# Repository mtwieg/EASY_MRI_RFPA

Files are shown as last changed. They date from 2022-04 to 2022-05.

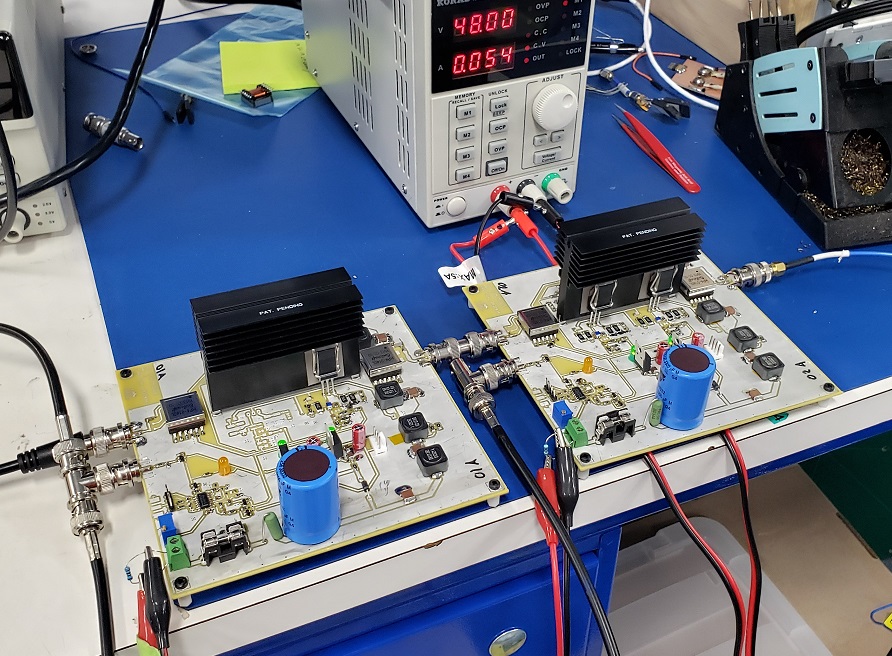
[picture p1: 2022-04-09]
Photos/full_test_setup.jpg

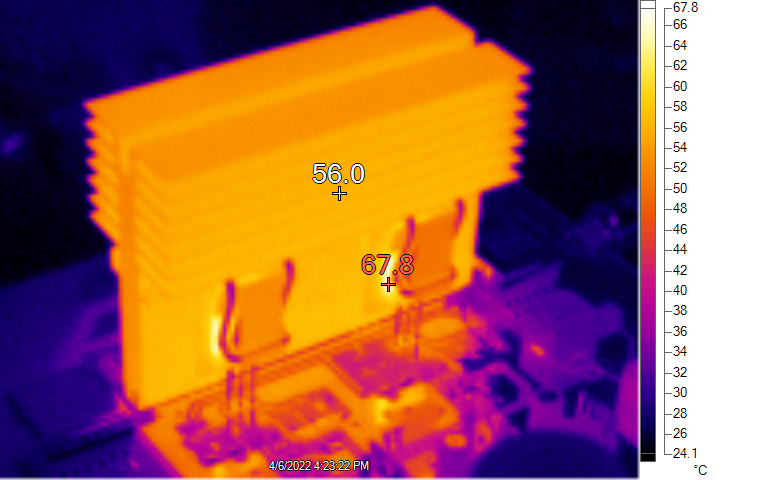
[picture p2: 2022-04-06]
Measurements and characterization/thermal_images_04_06_22/02_500us_20ms.png

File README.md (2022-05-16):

# EASY_MRI_RFPA
Click the "Wiki" tab above to view the tutorials and other info!

DISCLAIMER:
None of the designs in this repo have been tested or certified to any safety standards (IEC 60601-1, UL-94, etc). 
Intended for non-clinical, research use only.
Circuits may involve hazardous voltages, currents, and temperatures.
For non-expert users, I highly recommend never touching the circuitry while power is being applied. Circuitry may be probed, but probes should not be moved or tampered with while power is applied.

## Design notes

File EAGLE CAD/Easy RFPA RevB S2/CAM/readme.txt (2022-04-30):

Readme for Easy_RFPA_RevB_S2 CAM files
Mike Twieg, April 30, 2022

Material: FR4 1/16" finished thickness
Number of layers: 2
All copper layers 1oz
Surface finish: HASL
Soldermask (green) on both sides
Silkscreen (white) on both sides
Ignore silkscreen features which extend beyond the board dimensions, and which overlap with soldermask openings.

Panel description:
Board dimensions: 6.000" x 6.000", indicated on the outline layer
No array, boards to be fabbed 1-up

File list:
Easy_RFPA_RevB_S2(topcopper).cmp			Top copper layer
Easy_RFPA_RevB_S2(topmask).stc				Top soldermask layer
Easy_RFPA_RevB_S2(topsilk).plc				Top silk layer
Easy_RFPA_RevB_S2(toppaste).crc				Top paste layer
Easy_RFPA_RevB_S2(bottomcopper).sol			Bottom copper layer
Easy_RFPA_RevB_S2(bottommask).sts			Bottom soldermask layer
Easy_RFPA_RevB_S2(bottomsilk).pls			Bottom silk layer
Easy_RFPA_RevB_S2(bottompaste).crs			Bottom paste layer
Easy_RFPA_RevB_S2(Outline).art				Board outline
Easy_RFPA_RevB_S2(excellon).drd				NC drill file
Easy_RFPA_RevB_S2(excellon).dri				Drill list

All gerber files use 2.4 coordinate format, no zero suppression, absolute inches

Do not add any features or artwork without my written approval.

Regards,
[your info here]

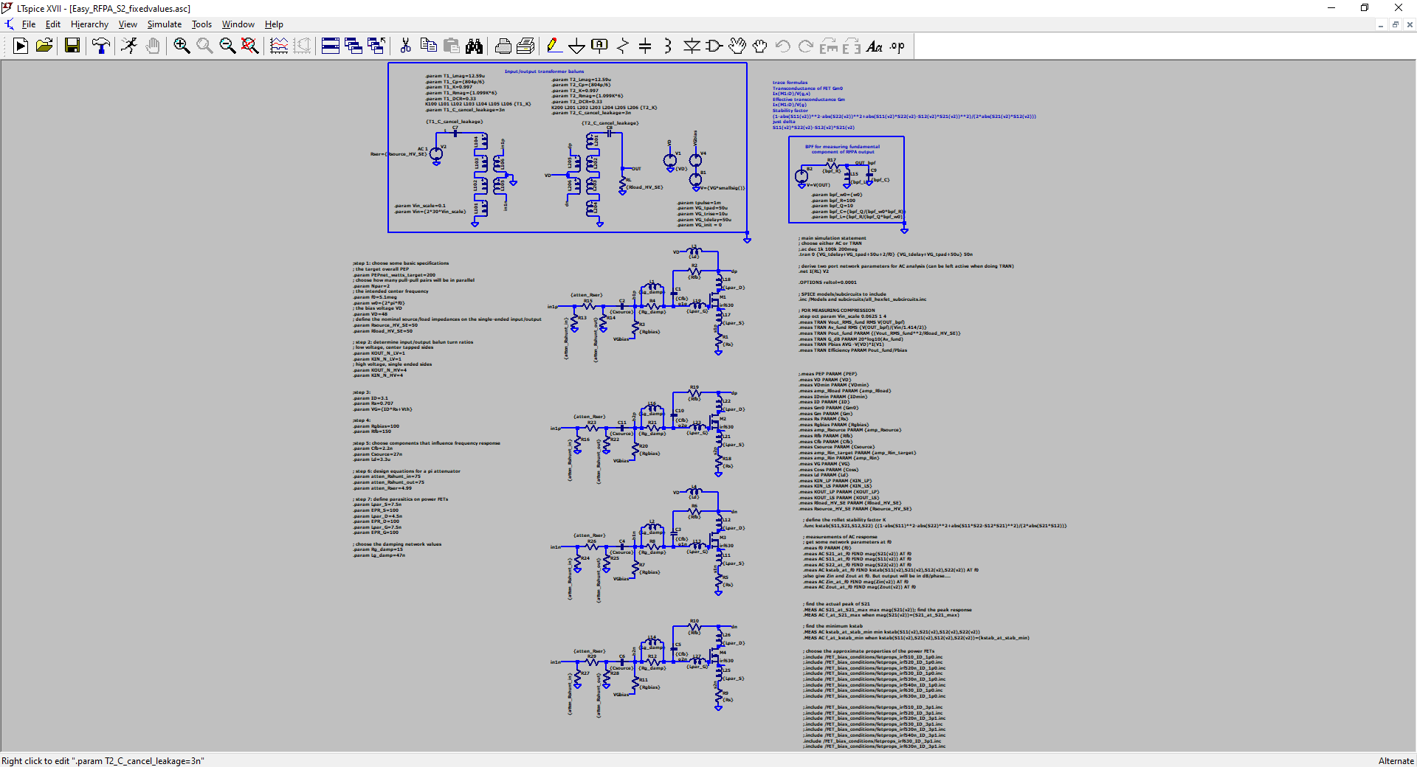
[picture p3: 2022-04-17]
LTSPICE simulations/pics for wiki/opened_schematic_screenshot.png

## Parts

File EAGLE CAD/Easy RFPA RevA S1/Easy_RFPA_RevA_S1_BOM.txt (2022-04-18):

Qty-1	Part References	Value	Package	Mfg Part Num	Mfg Name	VID	Vendor Part Num	Description	Pkg Code	XREF
2	"JP301, JP302"		1X02	***PART# '*' NOT FOUND***	*	*	*	*	*	*
3	"R101, R132, R314"	0	0805_IPC-7351B	***PART# '*' NOT FOUND***	*	*	*	*	*	*
4	"C101, C301, C305, C306"	0.1uF	0805_IPC-7351B	***PART# '*' NOT FOUND***	*	*	*	*	*	*
1	"C118"	0.1uF	C1812	***PART# '*' NOT FOUND***	*	*	*	*	*	*
1	"R405"	0.5	1206_IPC-7351B	***PART# '*' NOT FOUND***	*	*	*	*	*	*
1	"R404"	1.0	1206_IPC-7351B	***PART# '*' NOT FOUND***	*	*	*	*	*	*
2	"R402, R403"	1.0	R1206	***PART# '*' NOT FOUND***	*	*	*	*	*	*
1	"R401"	1.0	P0817V	PAC300001008FAC000	Vishay	DK	PPC3D1.0CT-ND	RES 1 OHM 3W 1% AXIAL	SMT	REF23
5	"R130, R131, R304, R308, R310"	1K	0805_IPC-7351B	***PART# '*' NOT FOUND***	*	*	*	*	*	*
2	"C112, C113"	2.2nF	C1206	***PART# '*' NOT FOUND***	*	*	*	*	*	*
2	"R118, R120"	2.74K	R2512	***PART# '*' NOT FOUND***	*	*	*	*	*	*
1	"R406"	2K	0805_IPC-7351B	***PART# '*' NOT FOUND***	*	*	*	*	*	*
1	"L401"	3.3UH	DR127	DR127-3R3-R	Eaton	DK	513-1221-6-ND	FIXED IND 3.3UH 10.5A 5.67 MOHM	SMT	REF21
2	"C406, C407"	4.7uF	C1206	***PART# '*' NOT FOUND***	*	*	*	*	*	*
2	"R104, R105"	4.99	1206_IPC-7351B	***PART# '*' NOT FOUND***	*	*	*	*	*	*
4	"R122, R123, R124, R125"	6.8	R2512	***PART# '*' NOT FOUND***	*	*	*	*	*	*
2	"C403, C404"	6.8uF	C1210	***PART# '*' NOT FOUND***	*	*	*	*	*	*
4	"R126, R127, R128, R129"	8.2	R2512	***PART# '*' NOT FOUND***	*	*	*	*	*	*
1	"R315"	10	0805_IPC-7351B	***PART# '*' NOT FOUND***	*	*	*	*	*	*
7	"R302, R303, R305, R306, R312, R317, R408"	10K	0805_IPC-7351B	***PART# '*' NOT FOUND***	*	*	*	*	*	*
1	"R301"	10K	RTRIM3299W	3299W-1-103LF	Bourns	DK	3299W-103LF-ND	TRIMMER 10K OHM 0.5W PC PIN TOP	TH	REF24
6	"C402, C405, C408, C411, C412, C413"	10UF	C2220_CKG57N	CGA9N3X7S2A106M230KE	TDK	DK	445-7995-6-ND	CAP CER 10UF 100V X7S 2220	2220	REF16
2	"C114, C115"	10nF	0805_IPC-7351B	***PART# '*' NOT FOUND***	*	*	*	*	*	*
2	"C105, C107"	12nF	0805_IPC-7351B	***PART# '*' NOT FOUND***	*	*	*	*	*	*
2	"R114, R115"	15	0805_IPC-7351B	***PART# '*' NOT FOUND***	*	*	*	*	*	*
2	"C409, C410"	22UF	E2,5-7	860010773010	Wurth	DK	732-8767-1-ND	CAP ALUM 22UF 20% 63V RADIAL	TH	REF18
3	"L103, L104, L402"	22UH	DR127	DR127-220-R	Eaton	DK	513-1044-6-ND	FIXED IND 22UH 4A 39.1 MOHM SMD	SMT	REF22
2	"C104, C106"	22nF	0805_IPC-7351B	***PART# '*' NOT FOUND***	*	*	*	*	*	*
1	"C304"	33pF	0805_IPC-7351B	***PART# '*' NOT FOUND***	*	*	*	*	*	*
2	"L101, L102"	47NH	L1008	1008CS-470XJLC	Coilcraft	MS	994-1008CS-470XJLC	Fixed Inductors 1008 47nH Unshld 5% 1A 160mOhms AECQ2	1008	REF20
1	"U301"	74AHC1G14DBV	SOT23-5	74AHC1G14QW5-7	Diodes Inc	DK	31-74AHC1G14QW5-7DKR-ND	IC INVERT SCHMITT 1CH 1-IN SOT25	SOT23-5	REF11
1	"R316"	100	0805_IPC-7351B	***PART# '*' NOT FOUND***	*	*	*	*	*	*
2	"R108, R110"	100	0805_IPC-7351B	***PART# '*' NOT FOUND***	*	*	*	*	*	*
2	"R109, R111"	100	1206_IPC-7351B	***PART# '*' NOT FOUND***	*	*	*	*	*	*
1	"R307"	100K	0805_IPC-7351B	***PART# '*' NOT FOUND***	*	*	*	*	*	*
1	"R309"	150	0805_IPC-7351B	***PART# '*' NOT FOUND***	*	*	*	*	*	*
4	"R102, R103, R106, R107"	220	1206_IPC-7351B	***PART# '*' NOT FOUND***	*	*	*	*	*	*
2	"R119, R121"	270	R2512	***PART# '*' NOT FOUND***	*	*	*	*	*	*
1	"R407"	590	0805_IPC-7351B	***PART# '*' NOT FOUND***	*	*	*	*	*	*
1	"C401"	3300UF	EB25D	MAL225638332E3	Vishay	DK	4651PHBK-ND	CAP ALUM 3300UF 20% 63V SNAP	TH	REF19
4	"J101, J102, J301, J302"	COAX112640BNC_EDGE	BNC_EDGE	112640	Amphenol	DK	ACX2259-ND	CONN BNC JACK STR 50OHM EDGE MNT	EDGE	REF25
1	"D401"	D-SCHOTTKYSK810L-TPSMC	DO-214AB(SMC)	SK810L-TP	Micro Commercial	DK	SK810L-TPMSDKR-ND	DIODE SCHOTTKY 100V 8A DO214AB	DO214AB	REF12
1	"D402"	D-ZENER1N5355B-TPDO15-12	DO15-12	1N5355B-TP	Micro Commercial	DK	1N5355BTPMSCT-ND	DIODE ZENER 18V 5W DO15	DO15	REF13
1	"F401"	FUSE_2P	02540121Z	02540121Z	Littelfuse	DK	F10144-ND	FUSE BLOK CARTRIDGE 400V 10A PCB	TH	REF30
1	"J401"	HDR_2X1282836-1282836-1	W237-02	282836-1	TE	DK	A135914-ND	TERM BLK 2POS SIDE ENTRY 5MM PCB	TH	REF27
2	"X407, X409"	HEATSINK_CLIPOMNI-220C	*	OMNI-220C	Wakefield-Vette	DK	345-1494-ND	UNIVERSAL TO-220 HEATSINK CLIP	NA	REF31
1	"X402"	HEATSINK_OMNI_DUALOMNI-UNI-30-75-D30-75-D	OMNI-UNI-30-75-D	OMNI-UNI-30-75-D	Wakefield-Vette	DK	345-1575-ND	HEATSINK TO-247 TO-264 TO-220	TH	REF29
2	"T101, T102"	HP4_TRAFO	HP4	HP4-0140LB	Coilcraft	Coilcraft	HP4-0140LB	Hexa-Path configurable magnetics high current SMT RoHS	SMT	REF1
2	"Q101, Q102"	IRF520N	TO220BV	IRF520NPBF	Infineon	DK	IRF520NPBF-ND	MOSFET N-CH 100V 9.7A TO220AB	TO220AB	REF4
1	"J402"	KK_PCFAN	47053-1000	47053-1000	MOLEX	DK	WM4330-ND	CONN HEADER VERT 4POS 2.54MM	TH	REF28
1	"U402"	LDO_3TERMMC78M05CTGTO220_VERT	TO220BV	MC78M05CTG	Onsemi	DK	MC78M05CTGOS-ND	IC REG LINEAR 5V 500MA TO220AB	TO220AB	REF9
1	"U401"	LDO_3TERMMC78M12CTGTO220_VERT	TO220BV	MC78M12CTG	Onsemi	DK	MC78M12CTGOS-ND	IC REG LINEAR 12V 500MA TO220AB	TO220AB	REF8
1	"LED301"	LEDHLMP-3401-E0002T1_3/4	LED5MM	HLMP-3401-E0002	Broadcom	DK	516-3193-1-ND	LED YELLOW DIFFUSED T-1 3/4 T/H	T-1 3/4	REF15
2	"LED401, LED402"	LEDHLMP-3962-F0002T1_3/4	LED5MM	HLMP-3962-F0002	Broadcom	DK	516-HLMP-3962-F0002CT-ND	LED GREEN DIFFUSED T-1 3/4 T/H	T-1 3/4	REF14
1	"Q301"	MOSFET_NBSS123SOT23	SOT23R_INFINEON	BSS123-7-F	Diodes Inc	DK	BSS123-FDICT-ND	MOSFET N-CH 100V 170MA SOT23-3	SOT23-3	REF5
1	"Q303"	NPNMMBT3904SOT23_BEC	SOT23R_INFINEON	MMBT3904,215	Nexperia	DK	1727-4044-6-ND	TRANS NPN 40V 200MA TO236AB	SOT23-3	REF6
1	"U302"	OPAMP_QUADTLV274IDSOIC14	SO14	TLV274ID	Texas Instruments	DK	296-26811-5-ND	IC OPAMP GP 4 CIRCUIT 14SOIC	14SOIC	REF10
1	"Q302"	PNPSOT23_BEC	SOT23R_INFINEON	PMBT3906,215	Nexperia	DK	1727-2960-6-ND	TRANS PNP 40V 200MA TO236AB	SOT23-3	REF7
2	"X403, X405"	THERMALPAD_TO220DC0011/15-TI900-0.12-0	*	DC0011/15-TI900-0.12-0	t-Global Technology	DK	1168-DC0011/15-TI900-0.12-0-ND	THERM PAD 21.84MMX18.79MM WHITE	NA	REF32

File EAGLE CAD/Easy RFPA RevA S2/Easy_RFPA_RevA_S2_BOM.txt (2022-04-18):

Qty-1	Part References	Value	Package	Mfg Part Num	Mfg Name	VID	Vendor Part Num	Description	Pkg Code	XREF
2	"JP301, JP302"		1X02	***PART# '*' NOT FOUND***	*	*	*	*	*	*
3	"R101, R132, R314"	0	0805_IPC-7351B	***PART# '*' NOT FOUND***	*	*	*	*	*	*
3	"C301, C305, C306"	0.1uF	0805_IPC-7351B	***PART# '*' NOT FOUND***	*	*	*	*	*	*
1	"R405"	0.5	1206_IPC-7351B	***PART# '*' NOT FOUND***	*	*	*	*	*	*
1	"R404"	1.0	1206_IPC-7351B	***PART# '*' NOT FOUND***	*	*	*	*	*	*
2	"R402, R403"	1.0	R1206	***PART# '*' NOT FOUND***	*	*	*	*	*	*
1	"R401"	1.0	P0817V	PAC300001008FAC000	Vishay	DK	PPC3D1.0CT-ND	RES 1 OHM 3W 1% AXIAL	SMT	REF23
7	"R130, R131, R229, R230, R304, R308, R310"	1K	0805_IPC-7351B	***PART# '*' NOT FOUND***	*	*	*	*	*	*
4	"C112, C113, C209, C210"	2.2nF	C1206	***PART# '*' NOT FOUND***	*	*	*	*	*	*
12	"R122, R123, R124, R125, R126, R127, R221, R222, R223, R224, R225, R226"	2.7	R2512	***PART# '*' NOT FOUND***	*	*	*	*	*	*
1	"R406"	2K	0805_IPC-7351B	***PART# '*' NOT FOUND***	*	*	*	*	*	*
4	"R128, R129, R227, R228"	3.3	R2512	***PART# '*' NOT FOUND***	*	*	*	*	*	*
3	"L103, L104, L401"	3.3UH	DR127	DR127-3R3-R	Eaton	DK	513-1221-6-ND	FIXED IND 3.3UH 10.5A 5.67 MOHM	SMT	REF21
1	"C103"	3nF	0805_IPC-7351B	***PART# '*' NOT FOUND***	*	*	*	*	*	*
1	"C120"	3nF	C1812	***PART# '*' NOT FOUND***	*	*	*	*	*	*
2	"C406, C407"	4.7uF	C1206	***PART# '*' NOT FOUND***	*	*	*	*	*	*
4	"R104, R105, R203, R204"	4.99	1206_IPC-7351B	***PART# '*' NOT FOUND***	*	*	*	*	*	*
2	"C403, C404"	6.8uF	C1210	***PART# '*' NOT FOUND***	*	*	*	*	*	*
1	"R315"	10	0805_IPC-7351B	***PART# '*' NOT FOUND***	*	*	*	*	*	*
7	"R302, R303, R305, R306, R312, R317, R408"	10K	0805_IPC-7351B	***PART# '*' NOT FOUND***	*	*	*	*	*	*
1	"R301"	10K	RTRIM3299W	3299W-1-103LF	Bourns	DK	3299W-103LF-ND	TRIMMER 10K OHM 0.5W PC PIN TOP	TH	REF24
6	"C402, C405, C408, C411, C412, C413"	10UF	C2220_CKG57N	CGA9N3X7S2A106M230KE	TDK	DK	445-7995-6-ND	CAP CER 10UF 100V X7S 2220	2220	REF16
4	"C114, C115, C211, C212"	10nF	0805_IPC-7351B	***PART# '*' NOT FOUND***	*	*	*	*	*	*
4	"R114, R115, R213, R214"	15	0805_IPC-7351B	***PART# '*' NOT FOUND***	*	*	*	*	*	*
2	"C409, C410"	22UF	E2,5-7	860010773010	Wurth	DK	732-8767-1-ND	CAP ALUM 22UF 20% 63V RADIAL	TH	REF18
1	"L402"	22UH	DR127	DR127-220-R	Eaton	DK	513-1044-6-ND	FIXED IND 22UH 4A 39.1 MOHM SMD	SMT	REF22
4	"C104, C106, C201, C203"	22nF	0805_IPC-7351B	***PART# '*' NOT FOUND***	*	*	*	*	*	*
4	"C105, C107, C202, C204"	27nF	0805_IPC-7351B	***PART# '*' NOT FOUND***	*	*	*	*	*	*
1	"C304"	33pF	0805_IPC-7351B	***PART# '*' NOT FOUND***	*	*	*	*	*	*
4	"L101, L102, L201, L202"	47NH	L1008	1008CS-470XJLC	Coilcraft	MS	994-1008CS-470XJLC	Fixed Inductors 1008 47nH Unshld 5% 1A 160mOhms AECQ2	1008	REF20
1	"U301"	74AHC1G14DBV	SOT23-5	74AHC1G14QW5-7	Diodes Inc	DK	31-74AHC1G14QW5-7DKR-ND	IC INVERT SCHMITT 1CH 1-IN SOT25	SOT23-5	REF11
8	"R102, R103, R106, R107, R201, R202, R205, R206"	75	1206_IPC-7351B	***PART# '*' NOT FOUND***	*	*	*	*	*	*
1	"R316"	100	0805_IPC-7351B	***PART# '*' NOT FOUND***	*	*	*	*	*	*
4	"R108, R110, R207, R209"	100	0805_IPC-7351B	***PART# '*' NOT FOUND***	*	*	*	*	*	*
4	"R109, R111, R208, R210"	100	1206_IPC-7351B	***PART# '*' NOT FOUND***	*	*	*	*	*	*
1	"R307"	100K	0805_IPC-7351B	***PART# '*' NOT FOUND***	*	*	*	*	*	*
1	"R309"	150	0805_IPC-7351B	***PART# '*' NOT FOUND***	*	*	*	*	*	*
4	"R119, R121, R218, R220"	270	R2512	***PART# '*' NOT FOUND***	*	*	*	*	*	*
4	"R118, R120, R217, R219"	330	R2512	***PART# '*' NOT FOUND***	*	*	*	*	*	*
1	"R407"	590	0805_IPC-7351B	***PART# '*' NOT FOUND***	*	*	*	*	*	*
1	"C401"	3300UF	EB25D	MAL225638332E3	Vishay	DK	4651PHBK-ND	CAP ALUM 3300UF 20% 63V SNAP	TH	REF19
4	"J101, J102, J301, J302"	COAX112640BNC_EDGE	BNC_EDGE	112640	Amphenol	DK	ACX2259-ND	CONN BNC JACK STR 50OHM EDGE MNT	EDGE	REF25
1	"D401"	D-SCHOTTKYSK810L-TPSMC	DO-214AB(SMC)	SK810L-TP	Micro Commercial	DK	SK810L-TPMSDKR-ND	DIODE SCHOTTKY 100V 8A DO214AB	DO214AB	REF12
1	"D402"	D-ZENER1N5355B-TPDO15-12	DO15-12	1N5355B-TP	Micro Commercial	DK	1N5355BTPMSCT-ND	DIODE ZENER 18V 5W DO15	DO15	REF13
1	"F401"	FUSE_2P	02540121Z	02540121Z	Littelfuse	DK	F10144-ND	FUSE BLOK CARTRIDGE 400V 10A PCB	TH	REF30
1	"J401"	HDR_2X1282836-1282836-1	W237-02	282836-1	TE	DK	A135914-ND	TERM BLK 2POS SIDE ENTRY 5MM PCB	TH	REF27
4	"X407, X408, X409, X410"	HEATSINK_CLIPOMNI-220C	*	OMNI-220C	Wakefield-Vette	DK	345-1494-ND	UNIVERSAL TO-220 HEATSINK CLIP	NA	REF31
1	"X402"	HEATSINK_OMNI_DUALOMNI-UNI-30-75-D30-75-D	OMNI-UNI-30-75-D	OMNI-UNI-30-75-D	Wakefield-Vette	DK	345-1575-ND	HEATSINK TO-247 TO-264 TO-220	TH	REF29
2	"T101, T102"	HP4_TRAFO	HP4	HP4-0140LB	Coilcraft	Coilcraft	HP4-0140LB	Hexa-Path configurable magnetics high current SMT RoHS	SMT	REF1
4	"Q101, Q102, Q201, Q202"	IRF630	TO220BV	IRF630	STMicroelectronics	DK	497-2757-5-ND	MOSFET N-CH 200V 9A TO220AB	TO220AB	REF3
1	"J402"	KK_PCFAN	47053-1000	47053-1000	MOLEX	DK	WM4330-ND	CONN HEADER VERT 4POS 2.54MM	TH	REF28
1	"U402"	LDO_3TERMMC78M05CTGTO220_VERT	TO220BV	MC78M05CTG	Onsemi	DK	MC78M05CTGOS-ND	IC REG LINEAR 5V 500MA TO220AB	TO220AB	REF9
1	"U401"	LDO_3TERMMC78M12CTGTO220_VERT	TO220BV	MC78M12CTG	Onsemi	DK	MC78M12CTGOS-ND	IC REG LINEAR 12V 500MA TO220AB	TO220AB	REF8
1	"LED301"	LEDHLMP-3401-E0002T1_3/4	LED5MM	HLMP-3401-E0002	Broadcom	DK	516-3193-1-ND	LED YELLOW DIFFUSED T-1 3/4 T/H	T-1 3/4	REF15
2	"LED401, LED402"	LEDHLMP-3962-F0002T1_3/4	LED5MM	HLMP-3962-F0002	Broadcom	DK	516-HLMP-3962-F0002CT-ND	LED GREEN DIFFUSED T-1 3/4 T/H	T-1 3/4	REF14
1	"Q301"	MOSFET_NBSS123SOT23	SOT23R_INFINEON	BSS123-7-F	Diodes Inc	DK	BSS123-FDICT-ND	MOSFET N-CH 100V 170MA SOT23-3	SOT23-3	REF5
1	"Q303"	NPNMMBT3904SOT23_BEC	SOT23R_INFINEON	MMBT3904,215	Nexperia	DK	1727-4044-6-ND	TRANS NPN 40V 200MA TO236AB	SOT23-3	REF6
1	"U302"	OPAMP_QUADTLV274IDSOIC14	SO14	TLV274ID	Texas Instruments	DK	296-26811-5-ND	IC OPAMP GP 4 CIRCUIT 14SOIC	14SOIC	REF10
1	"Q302"	PNPSOT23_BEC	SOT23R_INFINEON	PMBT3906,215	Nexperia	DK	1727-2960-6-ND	TRANS PNP 40V 200MA TO236AB	SOT23-3	REF7
4	"X403, X404, X405, X406"	THERMALPAD_TO220DC0011/15-TI900-0.12-0	*	DC0011/15-TI900-0.12-0	t-Global Technology	DK	1168-DC0011/15-TI900-0.12-0-ND	THERM PAD 21.84MMX18.79MM WHITE	NA	REF32

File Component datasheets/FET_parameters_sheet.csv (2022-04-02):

Name | Manufacturer | I have some | Datasheet link | Vdss | Package | Ciss (table) | Coss (table) | Crss (table) | Ciss (50V) | Coss (50V) | Crss (50V) | SOA current 50V 10ms | SOA current 50V 1ms | SOA current 50V 100us
IRF520N | IR + Infineon | Y |  | 100 | TO-220 | 330 | 92 | 54 | 310 | 70 | 45 | 1.3 | 3.6 | 14
IRF530PBF | Vishay | Y |  | 100 | TO-220 | 670 (wrong?) | 250 (wrong?) | 60 (wrong?) | 670 | 250 | 60 | 5.5 | 18 | 50
IRF530A | Fairchild + Onsemi | Y |  | 100 | TO-220 | 610 | 150 | 62 | 590 | 90 | 50 | 3 | 9 | 30
IRF530PBF | IR + Infineon | Y |  | 100 | TO-220 | 920 | 130 | 19 | 915 | 110 | 19 | 0.9 | 3.2 | 17
IRF630 | STM | Y |  | 100 | TO-220 | 370 | 77 | 14 | 370 | 53 | 11 | 1.9 | 6 | 20
IRF630 | Vishay | N |  | 100 |  | 800 | 240 | 76 | 750 | 175 | 30 | 4 | 12 | 38
IRF630NPBF | IR + Infineon | Y |  | 100 | TO-220 | 575 | 89 | 25 | 565 | 70 | 15 | 1.8 | 4 | 18

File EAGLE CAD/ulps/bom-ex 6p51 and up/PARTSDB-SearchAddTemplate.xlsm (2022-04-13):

Mfg Part Num | Mfg Name | VID | Vendor Part Num | Description | Pkg Code
C0805C105Z3VACTU | RoHS Compliant part | NE | 512-LM317T | Linear Voltage Regulators TO-220 1.5A ADJ VREG | *
C0805F474K3RACTU | Kemet | DK | 399-5112-1-ND | CAP CER .47UF 25V X7R 0805 FO | 0805
C0805C330J5GACTU | Kemet | DK | 399-1115-1-ND | CAP CERAMIC 33PF 50V NP0 0805 | 0805
C0805C471J5GACTU | Kemet | DK | 399-1133-1-ND | CAP CERAMIC 470PF 50V NP0 0805 | 0805
EEE-1CA101P | Panasonic - ECG | DK | PCE3879CT-ND | CAP ELECT 100UF 16V VS SMD | *
EEE-1EA471P | Panasonic - ECG | DK | PCE3909CT-ND | CAP ELECT 470UF 25V VS SMD | *
L78L33ACUTR | STMicroelectronics | DK | 497-1200-1-ND | IC REGULATOR POS 3.3V SOT89 | *
L7805ACD2T | STMicroelectronics | DK | 497-1440-5-ND | IC REG POS 1.5A 5V PREC D2PAK | *
LM324D | Texas Instruments | DK | 296-1390-5-ND | IC OPAMP GP 1.2MHZ QUAD 14SOIC | *
MAX3243ECPWR | Texas Instruments | DK | 296-19808-1-ND | IC RS232 3V-5.5V DRVR 28-TSSOP | *
TLC084CD | Texas Instruments | DK | 296-2423-5-ND | IC OPAMP GP 10MHZ QUAD 14SOIC | *
640454-2 | Tyco Electronics | DK | A19423-ND | CONN HEADER VERT 2POS .100 TIN | *
640454-8 | Tyco Electronics | DK | A19435-ND | CONN HEADER VERT 8POS .100 TIN | *
643813-2 | Tyco Electronics | DK | A23837-ND | CONN RECEPT 2POS 22AWG MTA100 | *
IRF614SPBF | Vishay/Siliconix | DK | IRF614SPBF-ND | MOSFET N-CH 250V 2.7A D2PAK | *
LM317T | Fairchild Semiconductor | DK | LM317TFS-ND | IC REG LDO ADJ 1.5A TO220-3 | *
LM317TG | ON SEMICONDUCTOR | NE | 98H0572 | ADJUSTABLE LDO VOLTAGE REGULATOR 1.2V TO 37V 1.5A TO220 ON SEMICONDUCTOR LM317TG | *
LM317T | Fairchild Semiconductor | ME | 512-LM317T | Linear Voltage Regulators TO-220 1.5A ADJ VREG | *
LM317TG | ON SEMICONDUCTOR | NE | 98H0572 | ADJUSTABLE LDO VOLTAGE REGULATOR 1.2V TO 37V 1.5A TO220 ON SEMICONDUCTOR LM317TG | *
LM317TG | ON SEMICONDUCTOR | NE | 98H0572 | ADJUSTABLE LDO VOLTAGE REGULATOR 1.2V TO 37V 1.5A TO220 ON SEMICONDUCTOR LM317TG | *
LM317TG | ON SEMICONDUCTOR | NE | 98H0572 | ADJUSTABLE LDO VOLTAGE REGULATOR 1.2V TO 37V 1.5A TO220 ON SEMICONDUCTOR LM317TG | *

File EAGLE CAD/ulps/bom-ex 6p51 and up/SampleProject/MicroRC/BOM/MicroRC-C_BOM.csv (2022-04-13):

Qty-1 | Part References | Value | Package | Mfg Part Num | Mfg Name | VID | Vendor Part Num | Description | Pkg Code | XREF
18 | C2, C8, C9, C10, C19, C20, C30, C31, C43, C57, C63, C69, C71, C72, C73, C75, C76, C77 | 0.1uF | C0805 | C0805F104K5RACTU | Kemet | DK | 399-5110-1-ND | CAP CER .1UF 50V X7R 0805 FO | 0805 | REF69
3 | C23, C24, C25 | 0.1uF | C1206 | C1206C104K5RACTU | Kemet | DK | 399-1249-1-ND | CAP .10UF 50V CERAMIC X7R 1206 | 1206 | REF67
0 | C78(DNP) | 0.1uF | C3216/T | DNP | DO NOT PLACE | (N/A) | DO NOT PLACE | DO NOT PLACE | * | REF14
1 | C55 | 0.1uF | C3216/T | T491A104K035AT | Kemet | DK | 399-3676-1-ND | CAPACITOR TANT .10UF 35V 10% SMD | * | REF22
1 | L2 | 0.1uH | L1206 | PM1210-R10J | JW Miller A Bourns Company | DK | M6093CT-ND | INDUCTOR .10UH 5% 1210 SMD | * | REF20
1 | C80 | 0.01uF | C1206 | 12065C103KAT2A | AVX Corporation | DK | 478-1542-1-ND | CAP CERM .01UF 10% 50V X7R 1206 | * | REF3
1 | C5 | 0.01uF | C0805 | C0805C103K5RACTU | Kemet | DK | 399-1158-1-ND | CAP 10000PF 50V CERAMIC X7R 0805 | 0805 | REF66
3 | C11, C12, C13 | 0.47uF | C0805 | C0805F474K3RACTU | Kemet | DK | 399-5112-1-ND | CAP CER .47UF 25V X7R 0805 FO | 0805 | REF74
2 | C40, C62 | 0.001uF | C0805 | C0805C102K5RACTU | Kemet | DK | 399-1147-1-ND | CAP 1000PF 50V CERAMIC X7R 0805 | 0805 | REF65
2 | C35, C38 | 0.047uF | C0805 | C0805C473K5RACTU | Kemet | DK | 399-1166-1-ND | CAP 47000PF 50V CERAMIC X7R 0805 | 0805 | REF68
1 | C41 | 0.0068uF | C0805 | C0805C682K5RACTU | Kemet | DK | 399-1157-1-ND | CAP 6800PF 50V CERAMIC X7R 0805 | 0805 | REF79
2 | R80, R81 | 0R | R0805 | RC0805JR-070RL | Yageo | DK | 311-0.0ARCT-ND | RES 0.0 OHM 1/8W 5% 0805 SMD | 0805 | REF92
2 | R82, R83 | 1.00K | R0805 | ERJ-6ENF1001V | Panasonic - ECG | DK | P1.00KCCT-ND | RES 1.00K OHM 1/8W 1% 0805 SMD | 0805 | REF45
4 | R16, R46, R55, R62 | 1M | R0805 | ERJ-6ENF1004V | Panasonic - ECG | DK | P1.00MCCT-ND | RES 1.00M OHM 1/8W 1% 0805 SMD | 0805 | REF46
14 | C1, C22, C39, C44, C45, C47, C50, C52, C58, C59, C61, C64, C65, C66 | 1uF | C0805 | C0805C105Z3VACTU | Kemet | DK | 399-1293-1-ND | CAP 1.0UF 25V CERAMIC Y5V 0805 | 0805 | REF73
1 | C67 | 1uF | C3216/T | T491A105K016AT | Kemet | DK | 399-3678-1-ND | CAPACITOR TANT 1.0UF 16V 10% SMD | * | REF23
1 | C56 | 2.2uF | C3216/T | T491A225K010AT | Kemet | DK | 399-3690-1-ND | CAPACITOR TANT 2.2UF 10V 10% SMD | * | REF24
1 | Y2 | 3.579 MHZ | TC310H | ECS-35-18-10X | ECS Inc | DK | XC1371-ND | CRYSTAL 3.579545 MHZ 18PF CYL | * | REF17
7 | R8, R9, R15, R17, R19, R30, R33 | 4.75K | R0805 | ERJ-6ENF4751V | Panasonic - ECG | DK | P4.75KCCT-ND | RES 4.75K OHM 1/8W 1% 0805 SMD | 0805 | REF55
1 | Y3 | 4.032MHZ | SM49 | ECS-40.3-20-5PX-TR | ECS Inc | DK | XC1258CT-ND | CRYSTAL 4.032MHZ 20PF SMD | * | REF16
1 | D2 | 5.1V | SOD123 | BZT52C5V1-7-F | Diodes Inc | DK | BZT52C5V1-FDITR-ND | DIODE ZENER 5.1V 500MW SOD-123 | SOD123 | REF10
1 | R36 | 5.62K | R0805 | ERJ-6ENF5621V | Panasonic - ECG | DK | P5.62KCCT-ND | RES 5.62K OHM 1/8W 1% 0805 SMD | 0805 | REF59
1 | R38 | 8.25K | R0805 | ERJ-6ENF8251V | Panasonic - ECG | DK | P8.25KCCT-ND | RES 8.25K OHM 1/8W 1% 0805 SMD | 0805 | REF61
1 | RN1 | 10K | 744-8 | 744C083103JPTR | CTS Resistor Products | DK | 744C083103JPCT-ND | RES ARRAY 10K OHM 8TERM 4RES SMD | * | REF8
19 | R5, R10, R11, R18, R25, R28, R39, R40, R43, R50, R54, R56, R57, R58, R65, R67, R69, R70, R79 | 10K | R0805 | ERJ-6ENF1002V | Panasonic - ECG | DK | P10.0KCCT-ND | RES 10.0K OHM 1/8W 1% 0805 SMD | 0805 | REF47
5 | R26, R27, R63, R71, R75 | 10K | EVME-SIDE | EVM-EGGA00B14 | Panasonic - ECG | DK | EGG14BK-ND | POT 10K OHM 6MM CERAMIC SIDE ADJ | * | REF42
2 | R2, R66 | 10K | EVM-L4G | EVM-L4GA00B14 | Panasonic - ECG | DK | L4G14BK-ND | POT 10K OHM 4MM CERAMIC TOP ADJ | * | REF44
2 | C4, C51 | 10uF | C0805 | C0805C106K9PACTU | Kemet | DK | 399-3138-1-ND | CAP CERAMIC 10UF 6.3V X5R 0805 | 0805 | REF72
3 | C3, C21, C79 | 10uF | C3528/T | T491B106M016AT | Kemet | DK | 399-3708-1-ND | CAPACITOR TANT 10UF 16V 20% SMD | * | REF25
1 | L4 | 10uH | PM-13 | PM3308-100M | JW Miller A Bourns Company | DK | M9719CT-ND | INDUCTOR POWER 10UH SMD | * | REF21
1 | R42 | 11.3K | R0805 | ERJ-6ENF1132V | Panasonic - ECG | DK | P11.3KCCT-ND | RES 11.3K OHM 1/8W 1% 0805 SMD | 0805 | REF49
1 | Y1 | 16.000 MHz | TC38H | ECS-160-18-9X | ECS Inc | DK | XC1383-ND | CRYSTAL 16.000 MHZ 18PF CYL | * | REF18
1 | D8 | 18V | SMB | 1SMB5931BT3G | ON Semiconductor | DK | 1SMB5931BT3GOSTR-ND | DIODE ZENER 18V 3W SMB | * | REF36
9 | R23, R31, R44, R48, R51, R59, R64, R72, R76 | 22K | R0805 | ERJ-6ENF2212V | Panasonic - ECG | DK | P22.1KCCT-ND | RES 22.1K OHM 1/8W 1% 0805 SMD | 0805 | REF51
2 | C6, C7 | 22pF | C0805 | C0805C220J5GACTU | Kemet | DK | 399-1113-1-ND | CAP CERAMIC 22PF 50V NP0 0805 | 0805 | REF71
3 | C68, C70, C74 | 22uF | C3528/T | T491B226M016AT | Kemet | DK | 399-3717-1-ND | CAPACITOR TANT 22UF 16V 20% SMD | * | REF26
1 | Y4 | 32.678 kHz | TC26H | ECS-.327-12.5-13X | ECS Inc | DK | X1124-ND | CRYSTAL 32.768 KHZ 12.5PF CYL | * | REF15
2 | R53, R60 | 33.2K | R0805 | ERJ-6ENF3322V | Panasonic - ECG | DK | P33.2KCCT-ND | RES 33.2K OHM 1/8W 1% 0805 SMD | 0805 | REF53
2 | C53, C54 | 33pF | C0805 | C0805C330J5GACTU | Kemet | DK | 399-1115-1-ND | CAP CERAMIC 33PF 50V NP0 0805 | 0805 | REF75
5 | R1, R3, R4, R12, R14 | 47.5R | R0805 | ERJ-6ENF47R5V | Panasonic - ECG | DK | P47.5CCT-ND | RES 47.5 OHM 1/8W 1% 0805 SMD | 0805 | REF57
1 | R6 | 48.7R | R2010 | ERJ-12SF48R7U | Panasonic - ECG | DK | P48.7ACCT-ND | RES 48.7 OHM 3/4W 1% 2010 SMD | 1210 | REF58
1 | R21 | 62K | R0805 | ERJ-6ENF6192V | Panasonic - ECG | DK | P61.9KCCT-ND | RES 61.9K OHM 1/8W 1% 0805 SMD | 0805 | REF60
1 | R24 | 91.0K | R0805 | ERJ-6ENF9092V | Panasonic - ECG | DK | P90.9KCCT-ND | RES 90.9K OHM 1/8W 1% 0805 SMD | 0805 | REF62
1 | R47 | 93.1K | R0805 | ERJ-6ENF9312V | Panasonic - ECG | DK | P93.1KCCT-ND | RES 93.1K OHM 1/8W 1% 0805 SMD | 0805 | REF63
13 | R13, R20, R34, R37, R41, R45, R49, R61, R68, R73, R74, R77, R78 | 100K | R0805 | ERJ-6ENF1003V | Panasonic - ECG | DK | P100KCCT-ND | RES 100K OHM 1/8W 1% 0805 SMD | 0805 | REF48
3 | C29, C46, C49 | 100pF | C0805 | C0805C101J5GACTU | Kemet | DK | 399-1122-1-ND | CAP CERAMIC 100PF 50V NP0 0805 | 0805 | REF64
1 | C28 | 100uF | CSV-E/F | EEE-1CA101P | Panasonic - ECG | DK | PCE3879CT-ND | CAP ELECT 100UF 16V VS SMD | * | REF80
1 | R35 | 150K | R0805 | ERJ-6ENF1503V | Panasonic - ECG | DK | P150KCCT-ND | RES 150K OHM 1/8W 1% 0805 SMD | 0805 | REF50
1 | X2 | 182-009-112-531 | NC182M9 | 182-009-113R531 | Norcomp Inc. | DK | 182-09ME-ND | CONN DB9 MALE .318"" R/A NICKEL | * | REF34
1 | R52 | 200K | EVME-SIDE | EVM-EGGA00B25 | Panasonic - ECG | DK | EGG25BK-ND | POT 200K OHM 6MM CERAM SIDE ADJ | * | REF43
1 | R32 | 301K | R0805 | ERJ-6ENF3013V | Panasonic - ECG | DK | P301KCCT-ND | RES 301K OHM 1/8W 1% 0805 SMD | 0805 | REF52
1 | R29 | 332K | R0805 | ERJ-6ENF3323V | Panasonic - ECG | DK | P332KCCT-ND | RES 332K OHM 1/8W 1% 0805 SMD | 0805 | REF54
1 | R7 | 464R | R1210 | ERJ-14NF4640U | Panasonic - ECG | DK | P464AACT-ND | RES 464 OHM 1/2W 1% 1210 SMD | 1210 | REF56
2 | C36, C37 | 470pF | C0805 | C0805C471J5GACTU | Kemet | DK | 399-1133-1-ND | CAP CERAMIC 470PF 50V NP0 0805 | 0805 | REF76
2 | C26, C27 | 470uF | CSV-G | EEE-1EA471P | Panasonic - ECG | DK | PCE3909CT-ND | CAP ELECT 470UF 25V VS SMD | * | REF81
1 | C48 | 560pF | C0805 | C0805C561J5GACTU | Kemet | DK | 399-1134-1-ND | CAP CERAMIC 560PF 50V NP0 0805 | 0805 | REF78
4 | C32, C33, C34, C42 | 1500pF | C0805 | C0805C152K5RACTU | Kemet | DK | 399-1150-1-ND | CAP 1500PF 50V CERAMIC X7R 0805 | 0805 | REF70
1 | C60 | 4700pF | C0805 | C0805C472K5RACTU | Kemet | DK | 399-1155-1-ND | CAP 4700PF 50V CERAMIC X7R 0805 | 0805 | REF77
1 | X3 | 70553-0007 | 70553-08 | 70553-0007 | Molex Connector Corporation | DK | WM4906-ND | CONN HEADER 8POS .100 R/A GOLD | * | REF30
1 | X5 | 640454-2 | MTA-100-2V | 640454-2 | Tyco Electronics | DK | A19423-ND | CONN HEADER VERT 2POS .100 TIN | * | REF87
1 | X4 | 640454-8 | MTA08-100 | 640454-8 | Tyco Electronics | DK | A19435-ND | CONN HEADER VERT 8POS .100 TIN | * | REF88
1 | U12 | AD158X | SOT23 | AD1584BRTZ-REEL7 | Analog Devices Inc | DK | AD1584BRTZ-REEL7CT-ND | IC V-REF 4.096V SOT-23 | SOT23 | REF1
1 | D1 | BAV16W-7-F | SOD123 | BAV16W-7-F | Diodes Inc | DK | BAV16W-FDICT-ND | DIODE SWITCH 75V 400MW SOD123 | SOD123 | REF9
0 | B1(DNP) | BR1225A/HB | BR1225 | BR1225A/HB | Panasonic - BCG | DK | P061-ND | BATTERY LITH COIN HITEMP W/LEGS | * | REF41
2 | D7, D10 | BZT52C5V1-7-F | SOD123 | BZT52C5V6-7-F | Diodes Inc | DK | BZT52C5V6-FDICT-ND | DIODE ZENER 5.6V 500MW SOD-123 | SOD123 | REF11
1 | S1 | CK-A | CK-A | 2M1-SP1-T2-B4-M6RE | Carling Technologies | DK | 432-1164-ND | SW TOGGLE SPDT .4VA RT ANG PCB | * | REF5
1 | L1 | CM1812 | CM1812 | CM1812R600R-10 | Laird-Signal Integrity Products | DK | 240-2454-1-ND | CHOKE COMMON MODE 60 OHMS SMD | * | REF27
1 | U6 | CM8870CS | SO18W | MT8870DS | Zarlink | FE | MT8870DS | DTMF Decoder IC | * | REF93
1 | U1 | DS1307Z | SO08 | DS1307Z+ | Maxim Integrated Products | DK | DS1307Z+-ND | IC RTC SERIAL 512K 8-SOIC | SO08 | REF28
1 | X1 | EDSTLZ951/2 | 951-2 | EDSTLZ951/2 | On Shore Technology Inc | DK | ED2427-ND | TERM BLOCK HDR 5.08MM 2POS PCB | * | REF39
1 | X1-MATE | EDZ951/2 | * | EDZ951/2 | On Shore Technology Inc | DK | ED2409-ND | TERM BLOCK PLUG 5.08MM 2POS | * | REF38
1 | L3 | FB-M1331 | L1206 | PM2001-200 | JW Miller A Bourns Company | DK | M1331CT-ND | FERRITE CHIP 20 OHM 25% | * | REF19
2 | Q3, Q4 | IRF614SPBF | D2PAK | IRF614SPBF | Vishay/Siliconix | DK | IRF614SPBF-ND | MOSFET N-CH 250V 2.7A D2PAK | * | REF90
1 | U9 | ISD4002S | SO28W | ISD4002-240SY | Nuvoton Technology Corporation | DK | ISD4002-240SY | IC VOICE REC/PLAY 240S 28-SOIC | * | REF35
1 | U4 | L78L33ACUTR | SOT89-4 | L78L33ACUTR | STMicroelectronics | DK | 497-1200-1-ND | IC REGULATOR POS 3.3V SOT89 | * | REF82
1 | U11 | L7805ACD2T | D2PAK | L7805ACD2T | STMicroelectronics | DK | 497-1440-5-ND | IC REG POS 1.5A 5V PREC D2PAK | * | REF83
1 | U5 | LM324D | SO14 | LM324D | Texas Instruments | DK | 296-1390-5-ND | IC OPAMP GP 1.2MHZ QUAD 14SOIC | * | REF84
1 | U7 | MAX323CSA | SO08 | MAX323CSA+ | Maxim Integrated Products | DK | MAX323CSA+-ND | IC SWITCH DUAL SPST 8SOIC | SO08 | REF29
1 | U3 | MAX3243IPWR | TSSOP28 | MAX3243ECPWR | Texas Instruments | DK | 296-19808-1-ND | IC RS232 3V-5.5V DRVR 28-TSSOP | * | REF85
1 | U2 | MEGA1281/2561 | TQFP64-AEB | ATMEGA1281-16AU | Atmel | DK | ATMEGA1281-16AU-ND | MCU AVR 128K FLASH 16MHZ 64TQFP | * | REF2
1 | PF1 | MF-SM030-2 | SMD-7555 | MF-SM030-2 | Bourns Inc. | DK | MF-SM030CT-ND | FUSE RESETTABLE .30A 60V SMD | * | REF4
2 | Q1, Q5 | MMBTA05LT1G | SOT23 | MMBTA05LT1G | ON Semiconductor | DK | MMBTA05LT1GOSCT-ND | TRANS DRIVER SS NPN 60V SOT23 | * | REF37
1 | U8 | MX828DS | SSOP24 | MX828DW | CML Electronics | MX | MX828DW | PL ENCODER/DECODER (DISCONTINUED!!!) | * | REF7
1 | R22 | NCP21WF104J03RA | R0805 | NCP21WF104J03RA | Murata Electronics North America | DK | 490-2451-1-ND | THERMISTOR 100K OHM NTC 0805 SMD | * | REF33
1 | D11 | RED | LED535 | 5350T5 | Chicago Miniature Lighting | DK | L20085-ND | LED GREEN T-3/4 RT ANG PCB | * | REF6
3 | D5, D6, D9 | S1GB-13 | SMB | RS1GB-13-F | Diodes Inc | DK | RS1GB-FDICT-ND | DIODE FAST RECOVERY 1A 400V SMB | SMB | REF12
1 | U10 | TL084D | SO14 | TLC084CD | Texas Instruments | DK | 296-2423-5-ND | IC OPAMP GP 10MHZ QUAD 14SOIC | * | REF86
1 | Q2 | ZXMN6A07Z | SOT89 | ZXMN6A07ZTA | Diodes/Zetex | DK | ZXMN6A07ZCT-ND | MOSFET N-CH 60V 1.9A SOT-89 | * | REF13

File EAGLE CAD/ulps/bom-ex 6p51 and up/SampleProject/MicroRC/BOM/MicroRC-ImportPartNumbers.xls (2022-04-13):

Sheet: Sheet1
PART-ID | VALUE | VID | VENDOR PART# | MFG PART#
R4 | 0R | DK | RHM0.0ACT-ND | MCR10EZHJ000
R21 | 100 | DK | P100ZCT-ND | ERA-6YEB101V
R12 | 390 | DK | P390ZCT-ND | ERA-6YEB391V
R3, R20 | 1.00k | DK | P1.00KCCT-ND | ERJ-6ENF1001V
R13 | 1.24k | DK | P1.24KCCT-ND | ERJ-6ENF1241V
R1 | 2.21k | DK | P2.21KCCT-ND | ERJ-6ENF2211V
R5, R7, R10, R15, R18, R26, R27, R28, R25 | 4.75k | DK | P4.75KCCT-ND | ERJ-6ENF4751V
R23 | 5.11k | DK | P5.11KCCT-ND | ERJ-6ENF5111V
R6, R16, R17, R24, R29, R33, R34 | 10.0k | DK | P10.0KCCT-ND | ERJ-6ENF1002V
R9, R11, R30, R31, R32 | 100k | DK | P100KCCT-ND | ERJ-6ENF1003V
R8 | 221k | DK | P221KCCT-ND | ERJ-6ENF2213V
R2, R14 | 1.20M | DK | P1.20MCCT-ND | ERJ-6ENF1204V
R19, R22 | 10M | DK | 311-10.0MCRCT-ND | RC0805FR-0710ML
R36, R37 | 20K LIN | DK | P3T9203-ND | EVU-E2JFK4B24
R35, R38 | 50K LIN | DK | P3T9503-ND | EVU-E2JFK4B54
C4, C5, C15, C21 | 0.1uF | DK | PCC1840CT-ND | ECJ-2YB1H104K
C2 | 0.1uF | DK | PCF1126CT-ND | ECP-U1C104MA5
C1, C14 | 0.15uF | DK | PCF1127CT-ND | ECP-U1C154MA5
C27 | 0.001uF | DK | PCC102BNCT-ND | ECJ-2VB1H102K
C3 | 0.0033uF | DK | PCF1334CT-ND | ECH-U1H332JX5
C8, C13, C18 | 47pF | DK | PCC470CGCT-ND | ECJ-2VC1H470J
C24 | (DNP)
C6, C7, C9, C10, C11, C12, C20, C22, C23, C26 | 10uF/25 | DK | PCE3795CT-ND | EEE-FK1E100R
C16, C17, C19, C25 | 220uF/25 | DK | PCE3800CT-ND | EEE-FK1E221P
L1, L2 | BLM21BD121SN1D | DK | 490-1044-1-ND | BLM21BD121SN1D
L3 | CM1812R600R-10 | DK | 240-2454-1-ND | CM1812R600R-10
U1, U2, U3 | TL082CDR | DK | 296-1284-1-ND | TL082CDR
Q1 | MMBF4416LT1G | DK | MMBF4416LT1GOSCT-ND | MMBF4416LT1G
Q2 | MMBT3906LT1 | DK | MMBT3906LT1INCT-ND | MMBT3906LT1
Q4 | MMBTA05LT1G | DK | MMBTA05LT1GOSCT-ND | MMBTA05LT1G
Q3, Q5 | NDS7002A | DK | NDS7002ACT-ND | NDS7002A
B2 | DF005S | DK | DF005SDI-ND | DF005S
D1 | BLUE | DK | 350-1562-ND | 521-9918F
D2,D3 | LTST-C170CKT | DK | 160-1176-1-ND | LTST-C170CKT
D4,D5 | MBR0520-TP | DK | MBR0520TPMSCT-ND | MBR0520-TP
D6 | BZT52C16-7-F | DK | BZT52C16-FDICT-ND | BZT52C16-7-F
D7 | 1N4148W-7-F | DK | 1N4148W-FDICT-ND | 1N4148W-7-F
T1 (XICON) | 42TL013-RC | ME | 42TL013-RC | 42TL013-RC
T1 (TRIAD) | SP-66 | DK | 237-1151-ND | SP-66
J3, J4 | NMJ6HCD2 | ME | 550-22302 | NMJ6HCD2
J7 (Header) | 640454-2 | DK | A19423-ND | 640454-2
J7 (Housing) | 3-643813-2 | DK | A31107-ND | 3-643813-2
S1 | SDA04H0SK | DK | CKN1328-ND | SDA04H0SK
KNOB | P670S-09-D6S | ME | 550-P82-90F | P670S-09-D6S
POWER ADAPTER | WDU18-200 | ME | 553-WDU18-200 | WDU18-200
POWER JACK | 722A | DK | SC1049-ND | 722A
MISC | 1590BB | AE | 806-1532 | 1590BB
MISC | ENCLOSURE
MISC | ENCLOSURE
 | VID
 | DK
 | ME
 | AE
 | CE

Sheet: Sheet2
Part Name | Part Number
C5 | ECJ-2VB1H103K
C41 | ECJ-2VB1H682K
C40, C62 | ECJ-2VB1H102K
C2, C8, C9, C10, C19, C20, C30, C31, C43, C57, C63, C69, C71, C72, C73, C75, C76, C77 | ECJ-2VB1C473K
C35, C38 | ECJ-2VB1C473K
C60 | ECJ-2VB1H472K
C11, C12, C13 | ECJ-2FF1E474Z
C1, C22, C39, C44, C45, C47,C50, C52, C58, C59, C61, C64 | ECJ-2FB1E225K
C65, C66 | ECJ-2FB1E225K
C6, C7 | ECJ-2VC1H220J
C53, C54 | ECJ-2VC1H330J
C4, C51 | ECJ-2FB0J106M
C29, C46, C49 | ECJ-2VC1H101J
C36, C37 | ECJ-2VC1H471J
C48 | ECJ-2VC1H561J
C32, C33, C34, C42 | ECJ-2VB2A152K
C23, C24, C25 | ECJ-3VB1H104K
C80 | 12065C103KAT2A
C55, C78 | T491A104K035AT
C67 | T491A105K016AT
C56 | T491A225K010AT
C3, C21, C79 | T491B106M016AT
C68, C70, C74 | T491B226M016AT
C28 | EEE-1CA101P
C26, C27 | EEE-1EA471P
R80, R81 | RC0805JR-070RL
R1, R3, R4, R12 | ERJ-6ENF47R5V
R8, R9, R15, R17, R19, R30, R33 | ERJ-6ENF4751V
R36 | ERJ-6ENF5621V
R38 | ERJ-6ENF8251V
R5, R10, R11, R14, R18, R25, R28, R39, R40, R43, R50, R54, R56, R57, R58, R65, R67, R69, R70, R79 | ERJ-6ENF1002V
R42 | ERJ-6ENF1132V
R23, R31, R44, R48, R51, R59, R64, R72, R76 | ERJ-6ENF2212V
R53, R60 | ERJ-6ENF3322V
R21 | ERJ-6ENF6192V
R24 | ERJ-6ENF9092V
R47 | ERJ-6ENF9312V
R13, R20, R34, R37, R41, R45, R49, R61, R68, R73, R74, R77, R78 | ERJ-6ENF1003V
R35 | ERJ-6ENF1503V
R32 | ERJ-6ENF3013V
R29 | ERJ-6ENF3323V
R16, R46, R55, R62 | ERJ-6ENF1004V
R7 | ERJ-14NF4640U
R6 | ERJ-12SF48R7U
R22 | NCP21WF104J03RA
RN1 | 744C083103JPTR
R26, R27, R63, R71, R75 | EVM-EGGA00B14
R52 | EVM-EGGA00B25
R2, R66 | EVM-L4GA00B14
Q1, Q5 | MMBTA05LT1G
Q2 | ZXMN6A07ZTA
Q3, Q4 | IRF614SPBF
U11 | L7805ACD2T
U1 | DS1307Z+
U9 | ISD4002-240SY
U4 | L78L33ACUTR
U6 | MT8870DS
U5 | LM324D
U3 | MAX3243ECPWR
U7 | MAX323CSA+
U2 | ATMEGA1281-16AU
U8 | MX828DW
U10 | TLC084CD
U12 | AD1584BRTZ-REEL7
D5, D6, D9 | RS1GB-13-F
D1 | BAV16W-7-F
D7, D10 | BZT52C5V6-7-F
D11 | 5350T5
L1 | CM1812R600R-10
L2 | PM1210-R10J
L3 | PM2001-200
L4 | PM3308-100M
Y1 | ECS-160-18-9X
Y2 | ECS-35-18-10X
Y3 | ECS-40.3-20-5PX-TR
Y4 | ECS-.327-12.5-13X
DS1 | DMC-20261NY-LY-CCE-CMN
B1 | BR1225A/HB
PF1 | MF-SM030-2
S2 | 2M1-SP1-T2-B4-M6RE
X1 | EDSTLZ951/2
X2 | 182-009-113R531
X3 | 70553-0007
X4 | 640454-2

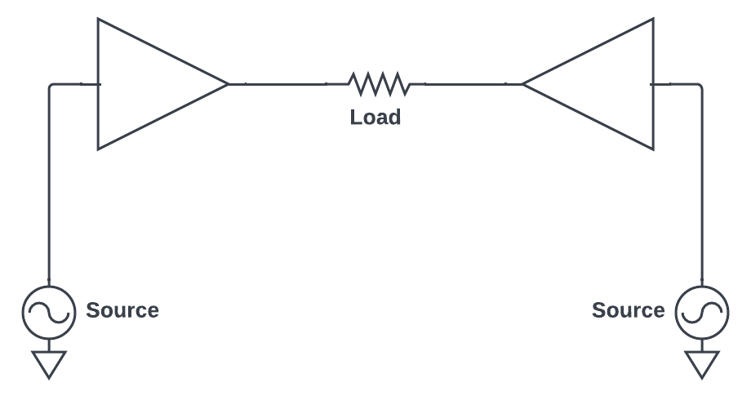
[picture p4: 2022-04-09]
materials for slides/rfpa_combination_diagrams - pushpull splitsources.png

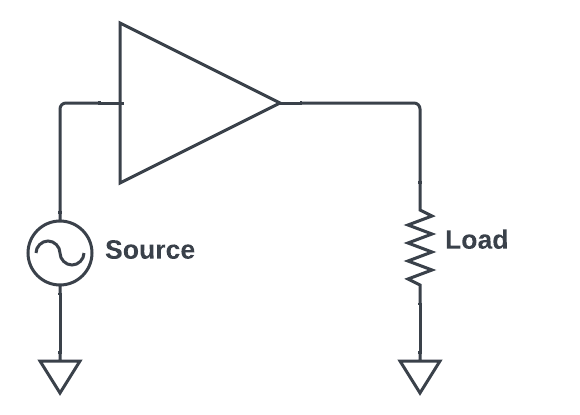
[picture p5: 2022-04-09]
materials for slides/rfpa_combination_diagrams - singleamp.png

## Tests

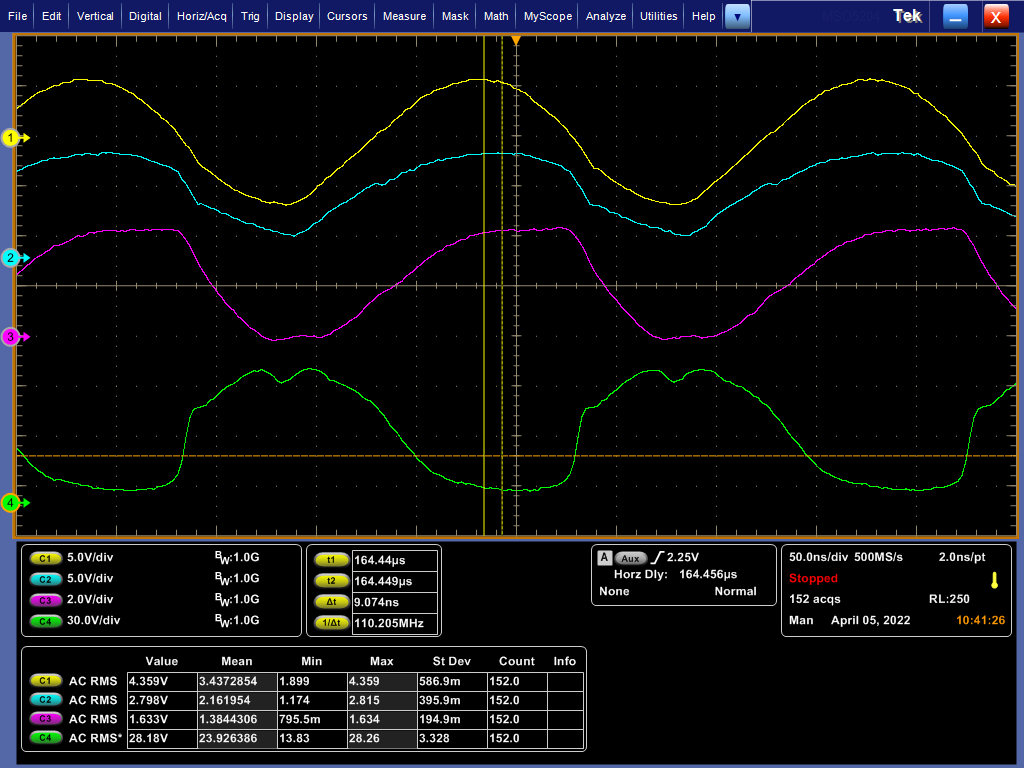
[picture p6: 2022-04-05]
Measurements and characterization/scope_captures_04_05_22/030_rfpa02_zoom_22dBm000.png

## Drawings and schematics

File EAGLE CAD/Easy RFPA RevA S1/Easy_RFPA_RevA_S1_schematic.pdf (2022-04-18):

A

A

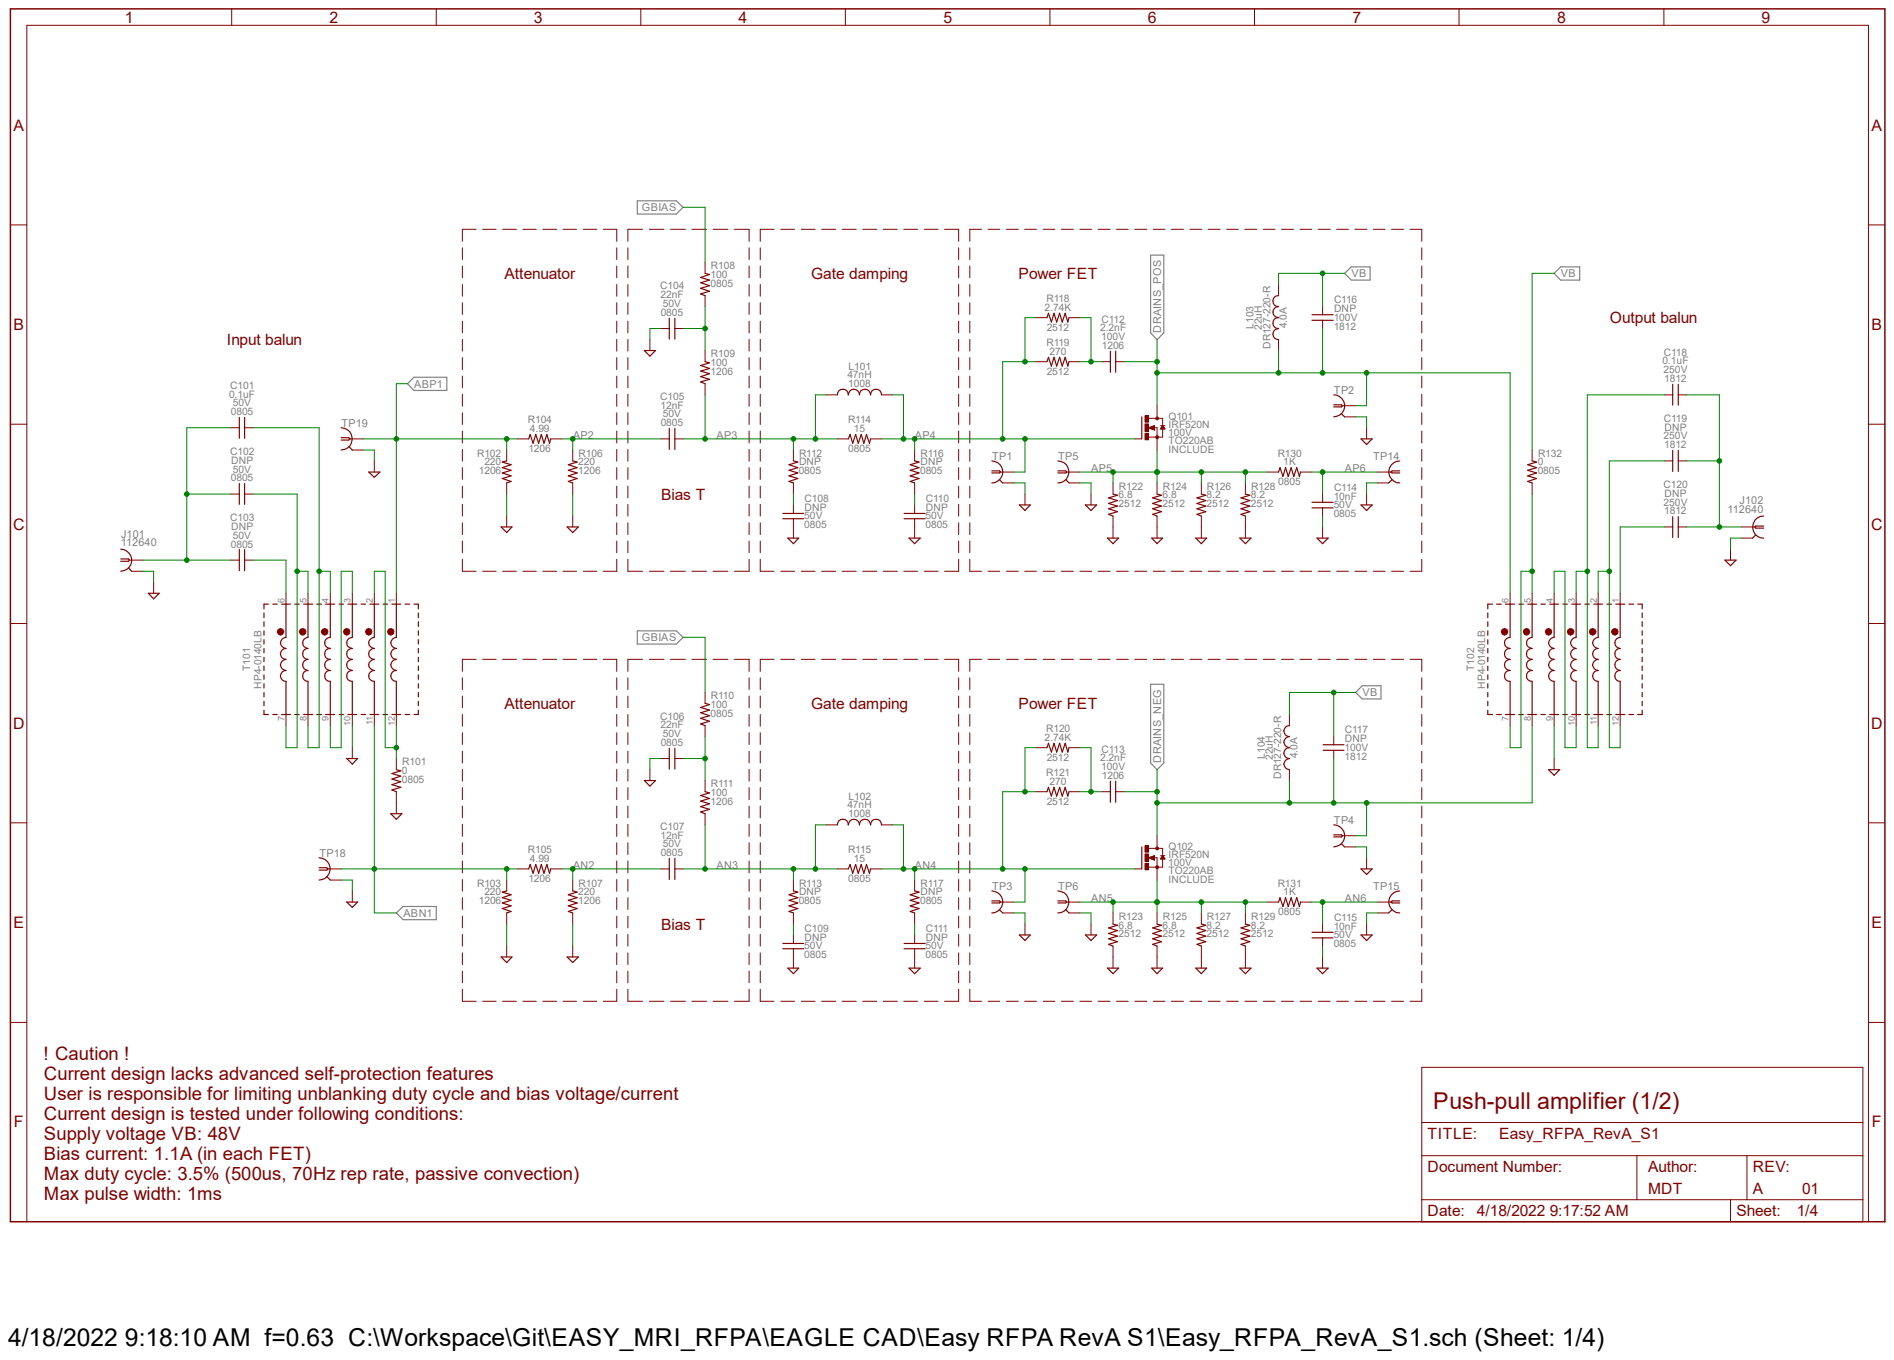
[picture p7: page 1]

! Caution !
Current design lacks advanced self-protection features
User is responsible for limiting unblanking duty cycle and bias voltage/current
Current design is tested under following conditions:
Supply voltage VB: 48V
Bias current: 1.1A (in each FET)
Max duty cycle: 3.5% (500us, 70Hz rep rate, passive convection)
Max pulse width: 1ms

Document Number: | Author: MDT | REV: 01 A

Date: 4/18/2022 9:17:52 AM | Sheet: 1/4

4/18/2022 9:18:10 AM f=0.63 C:\Workspace\Git\EASY_MRI_RFPA\EAGLE CAD\Easy RFPA RevA S1\Easy_RFPA_RevA_S1.sch (Sheet: 1/4)

A

A

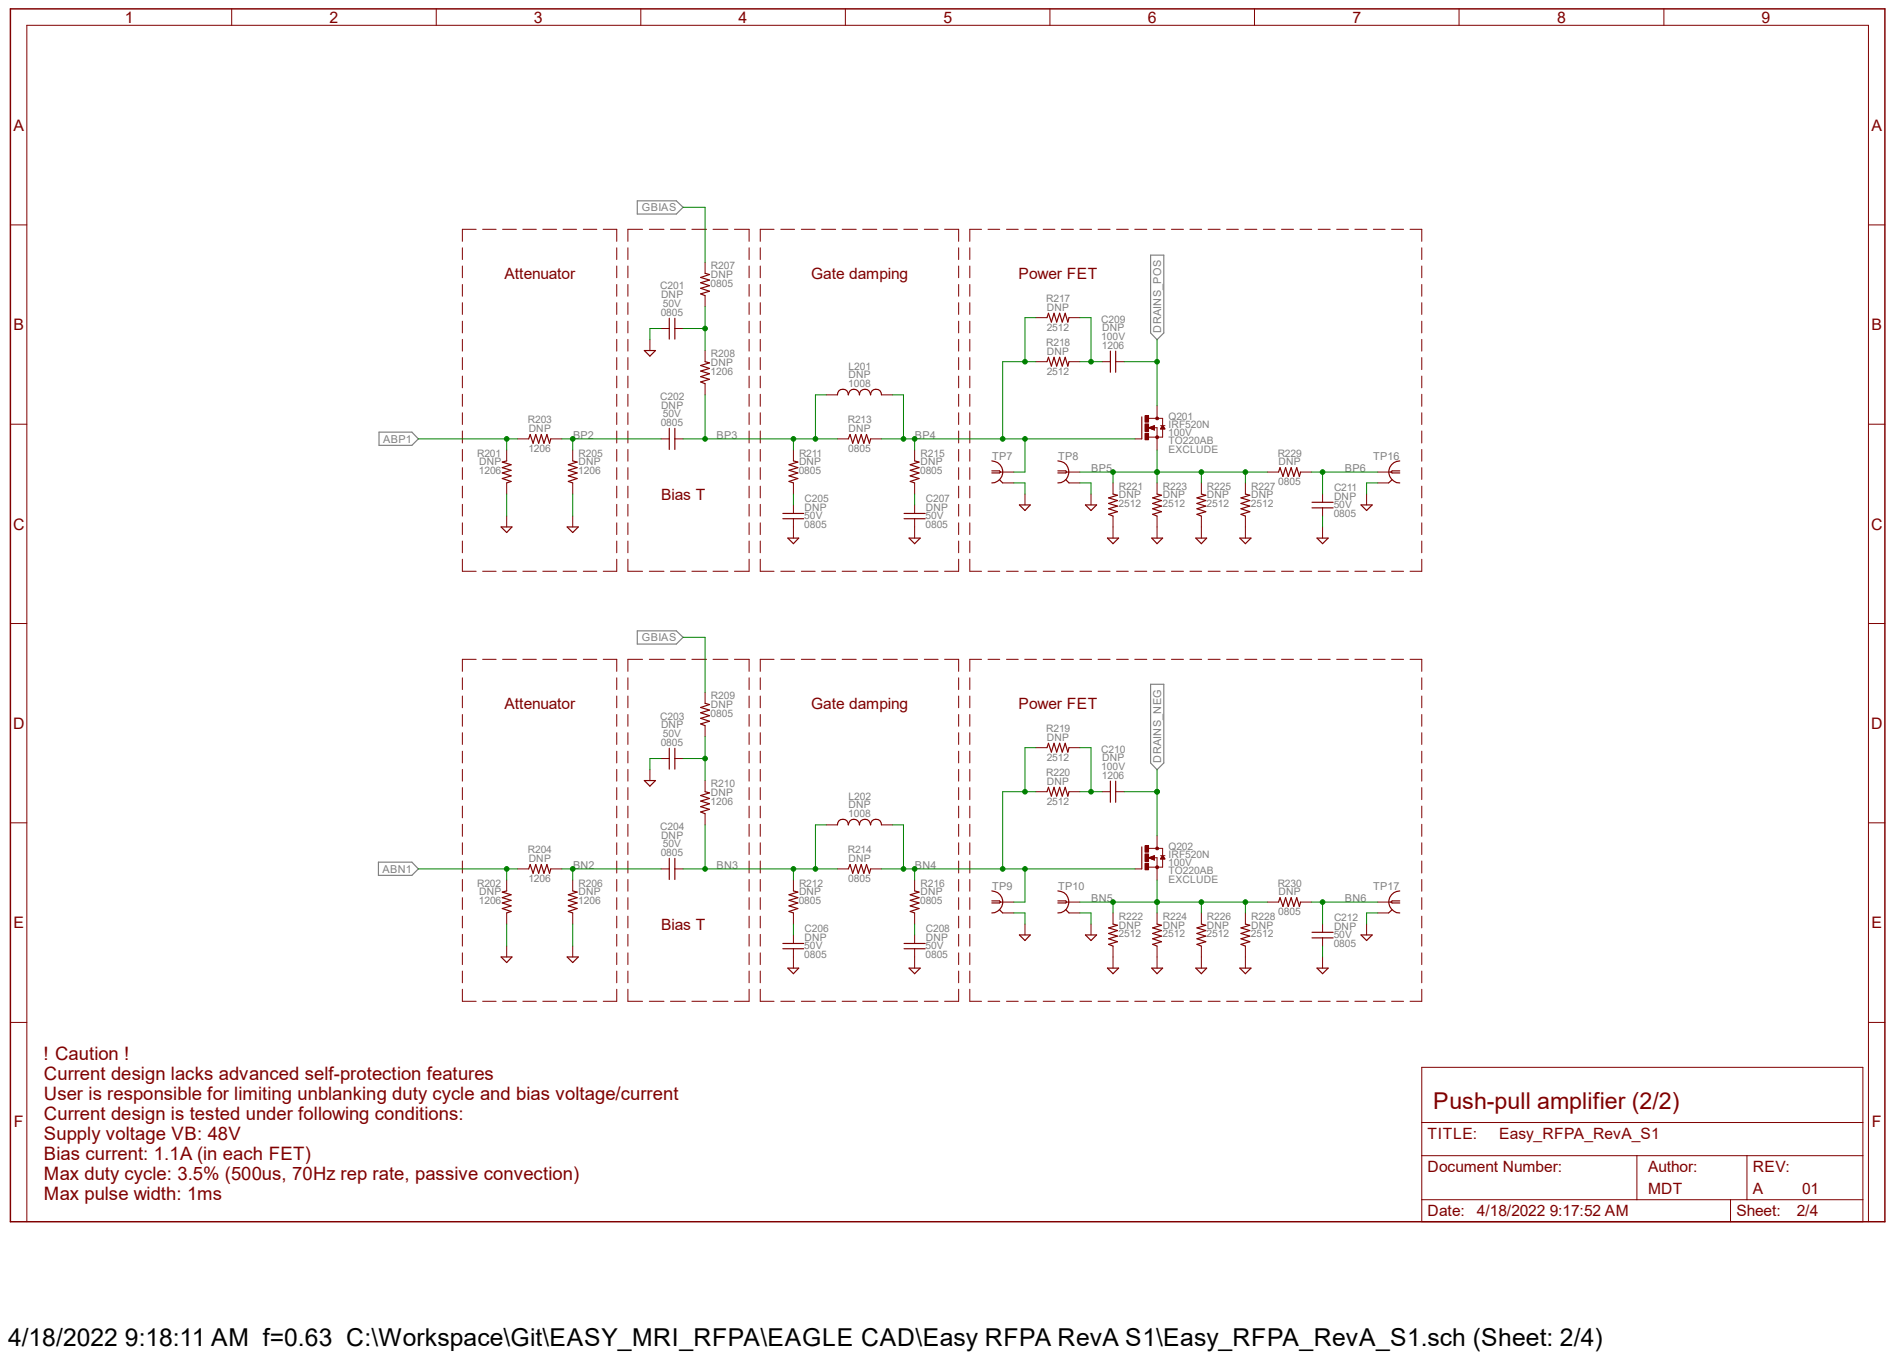
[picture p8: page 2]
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

Document Number: | Author: MDT | REV: 01 A

Date: 4/18/2022 9:17:52 AM | Sheet: 2/4

4/18/2022 9:18:11 AM f=0.63 C:\Workspace\Git\EASY_MRI_RFPA\EAGLE CAD\Easy RFPA RevA S1\Easy_RFPA_RevA_S1.sch (Sheet: 2/4)

If not using analog input,

A

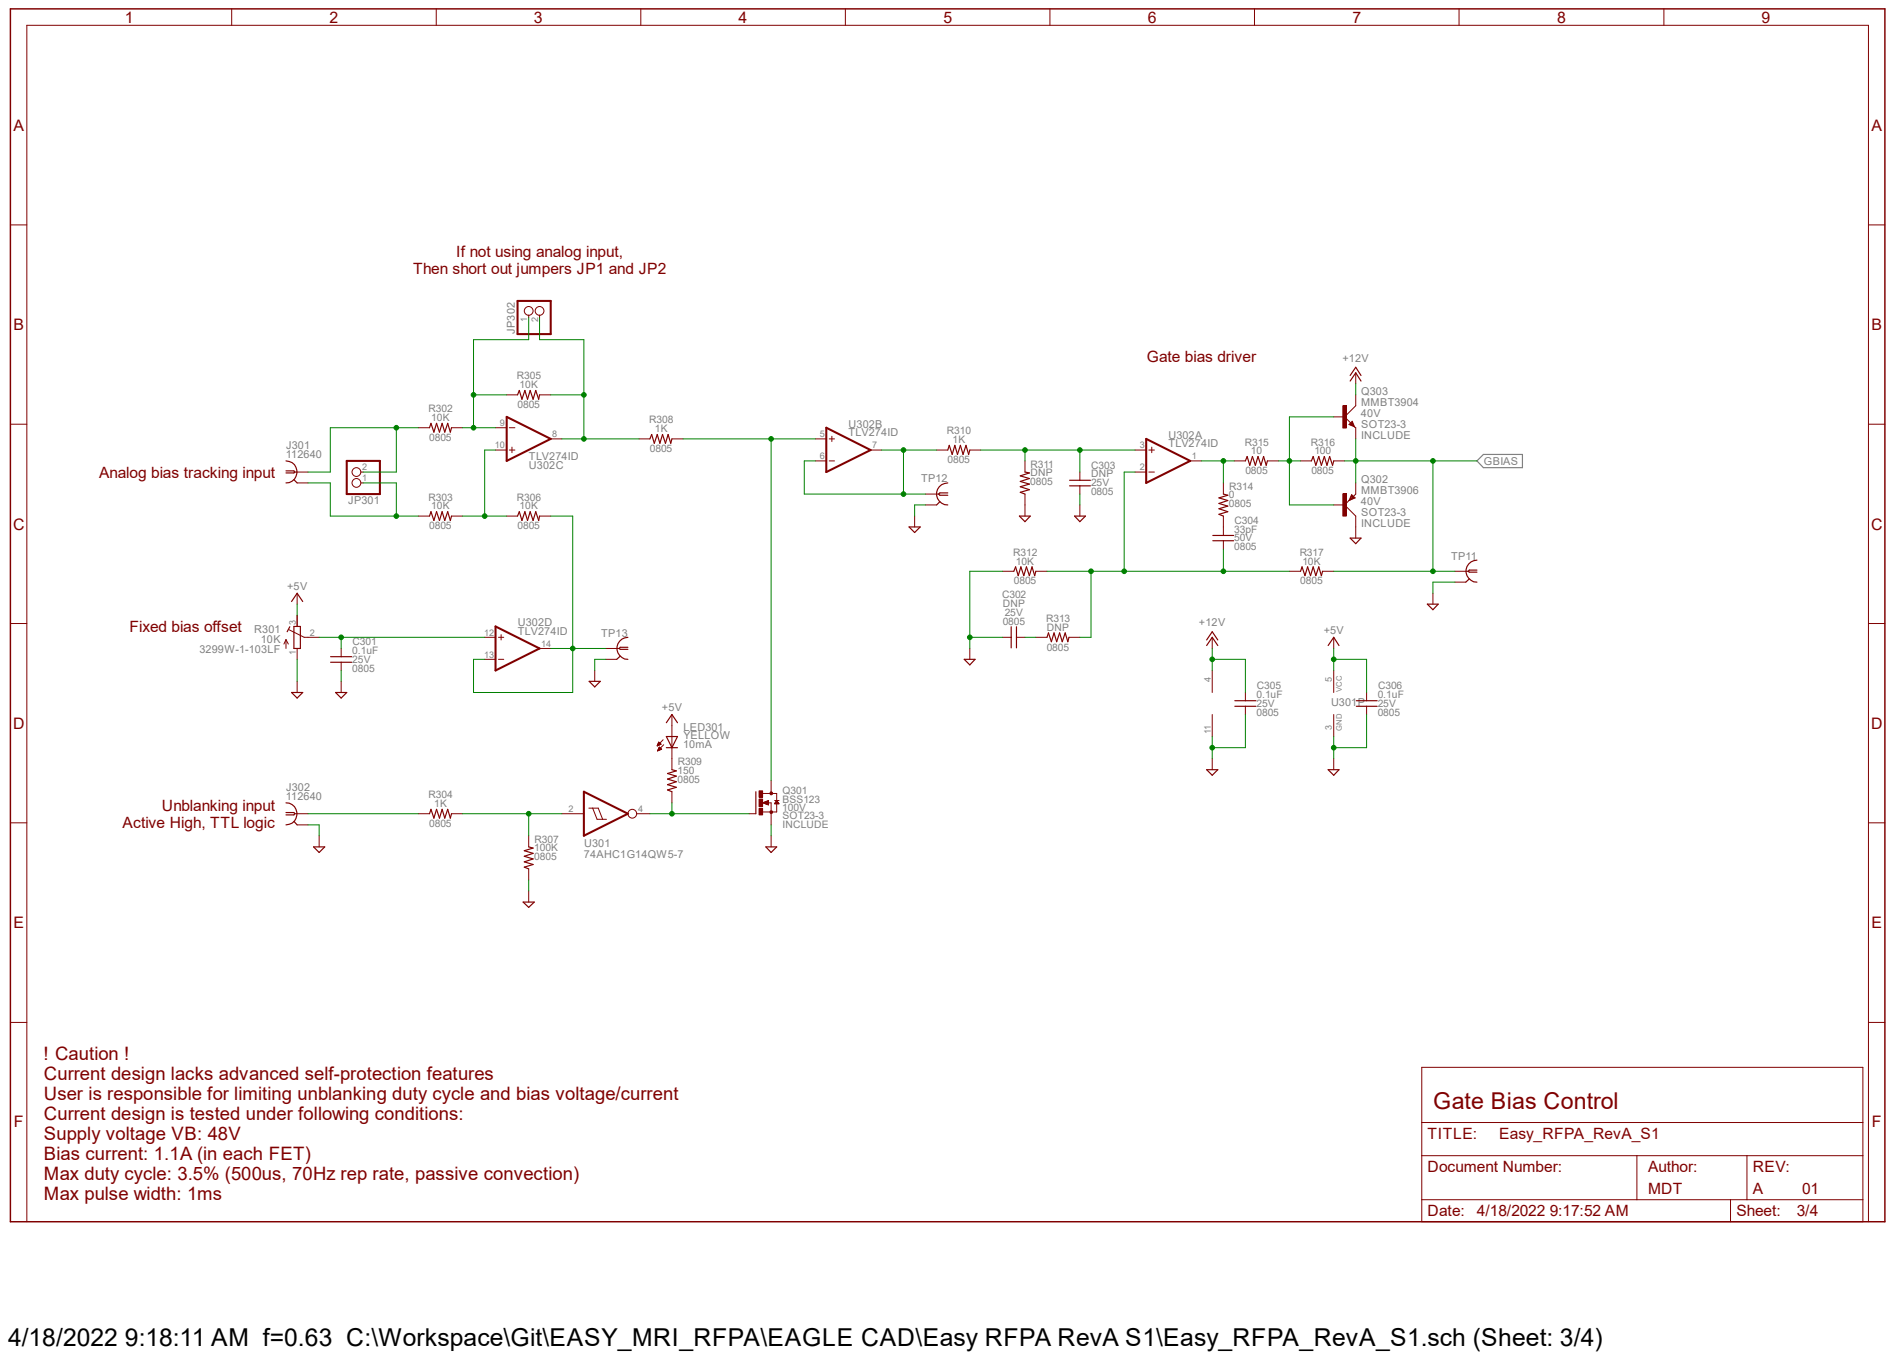
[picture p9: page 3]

Then short out jumpers JP1 and JP2

Analog bias tracking input

Unblanking input
Active High, TTL logic

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

Document Number: | Author: MDT | REV: 01 A

Date: 4/18/2022 9:17:52 AM | Sheet: 3/4

4/18/2022 9:18:11 AM f=0.63 C:\Workspace\Git\EASY_MRI_RFPA\EAGLE CAD\Easy RFPA RevA S1\Easy_RFPA_RevA_S1.sch (Sheet: 3/4)

A

A

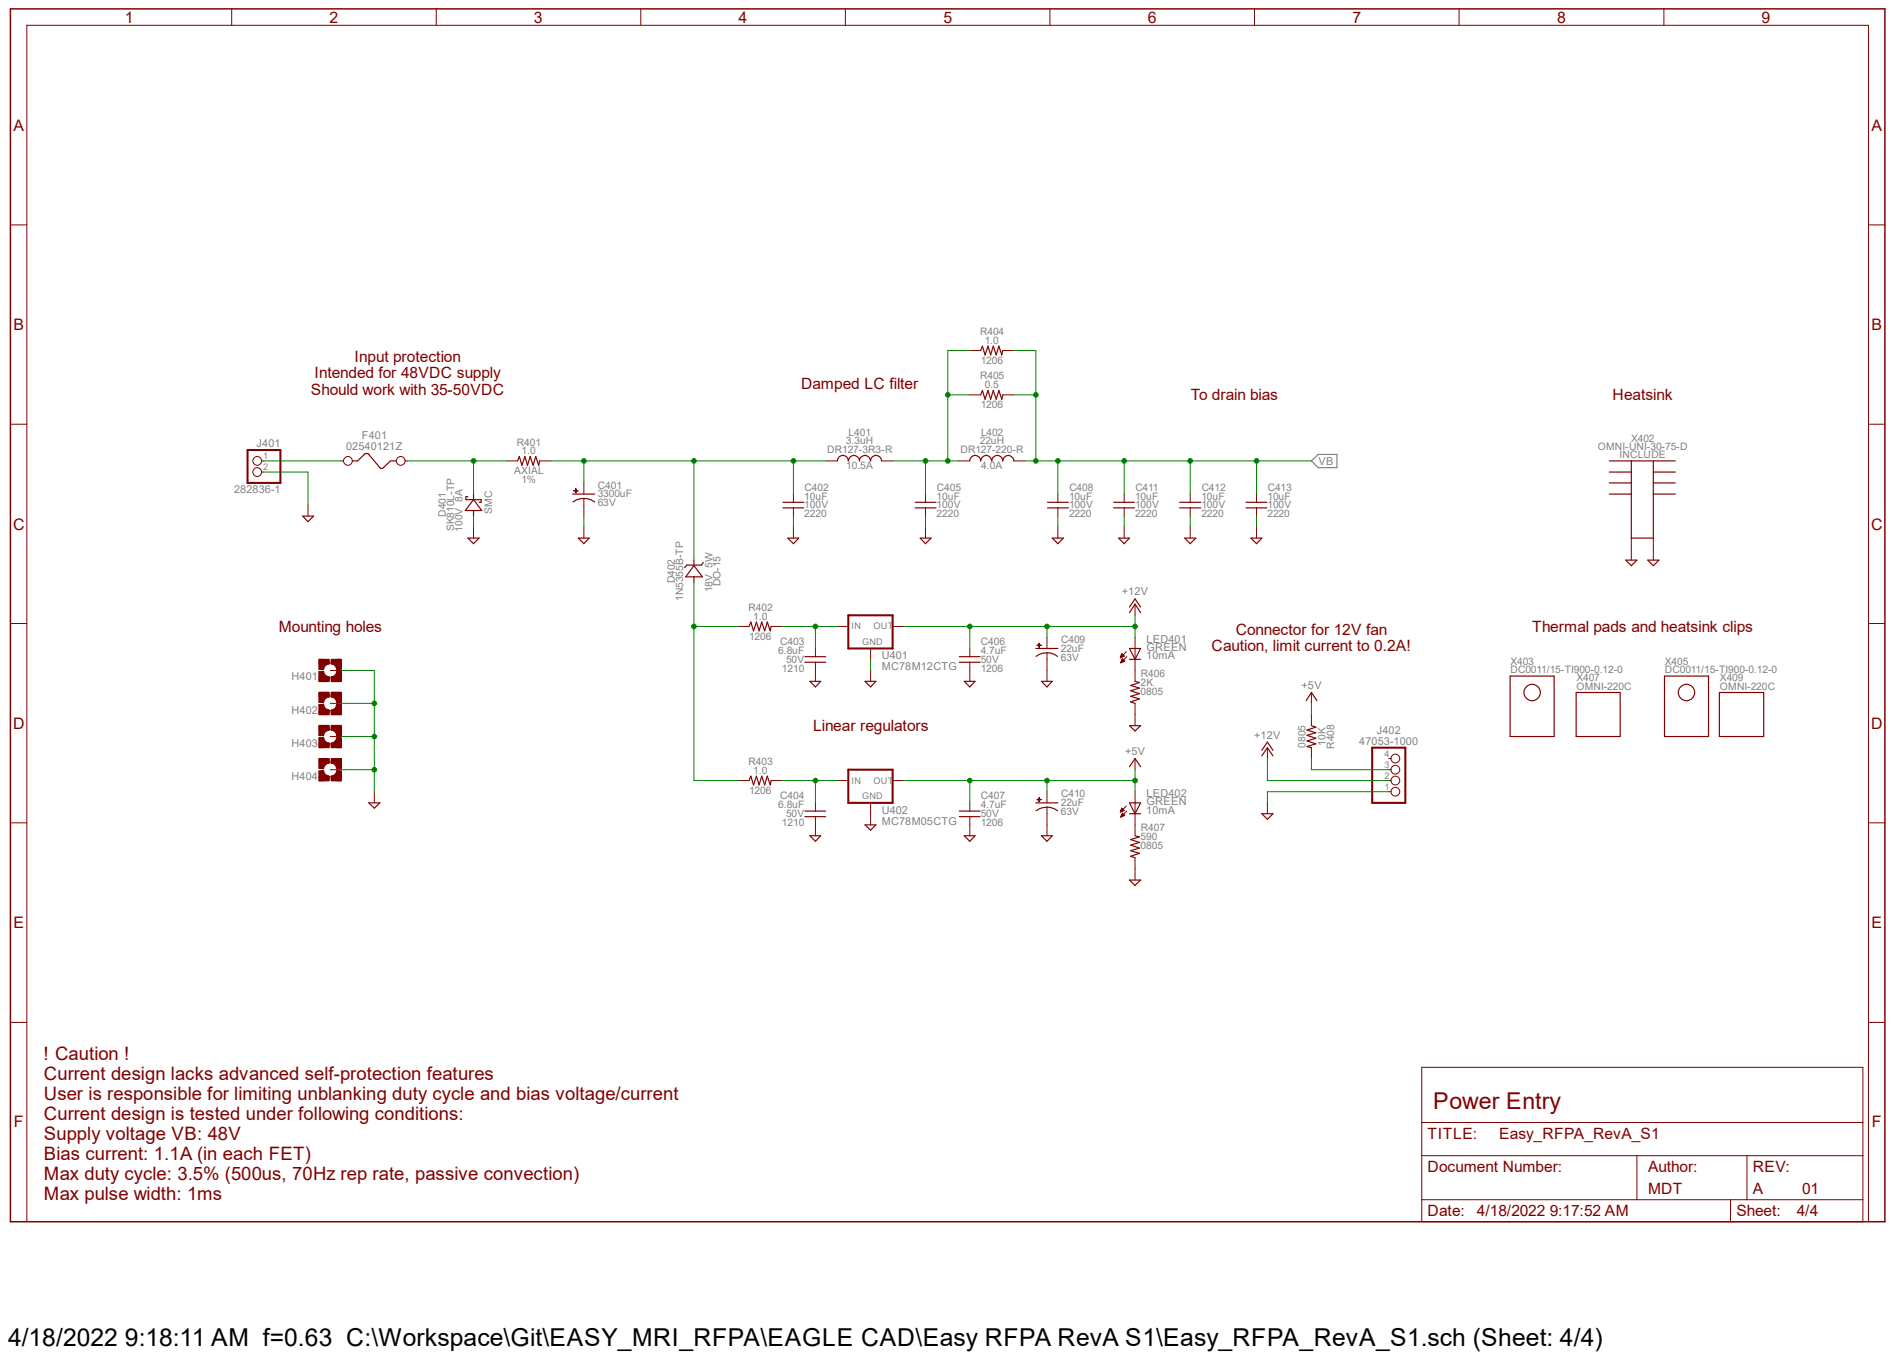
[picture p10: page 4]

Thermal pads and heatsink clips

Connector for 12V fan
Caution, limit current to 0.2A!

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

Document Number: | Author: MDT | REV:

Date: 4/18/2022 9:17:52 AM | Sheet: 4/4

4/18/2022 9:18:11 AM f=0.63 C:\Workspace\Git\EASY_MRI_RFPA\EAGLE CAD\Easy RFPA RevA S1\Easy_RFPA_RevA_S1.sch (Sheet: 4/4)

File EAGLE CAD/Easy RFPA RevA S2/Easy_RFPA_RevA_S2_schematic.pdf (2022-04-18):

A

A

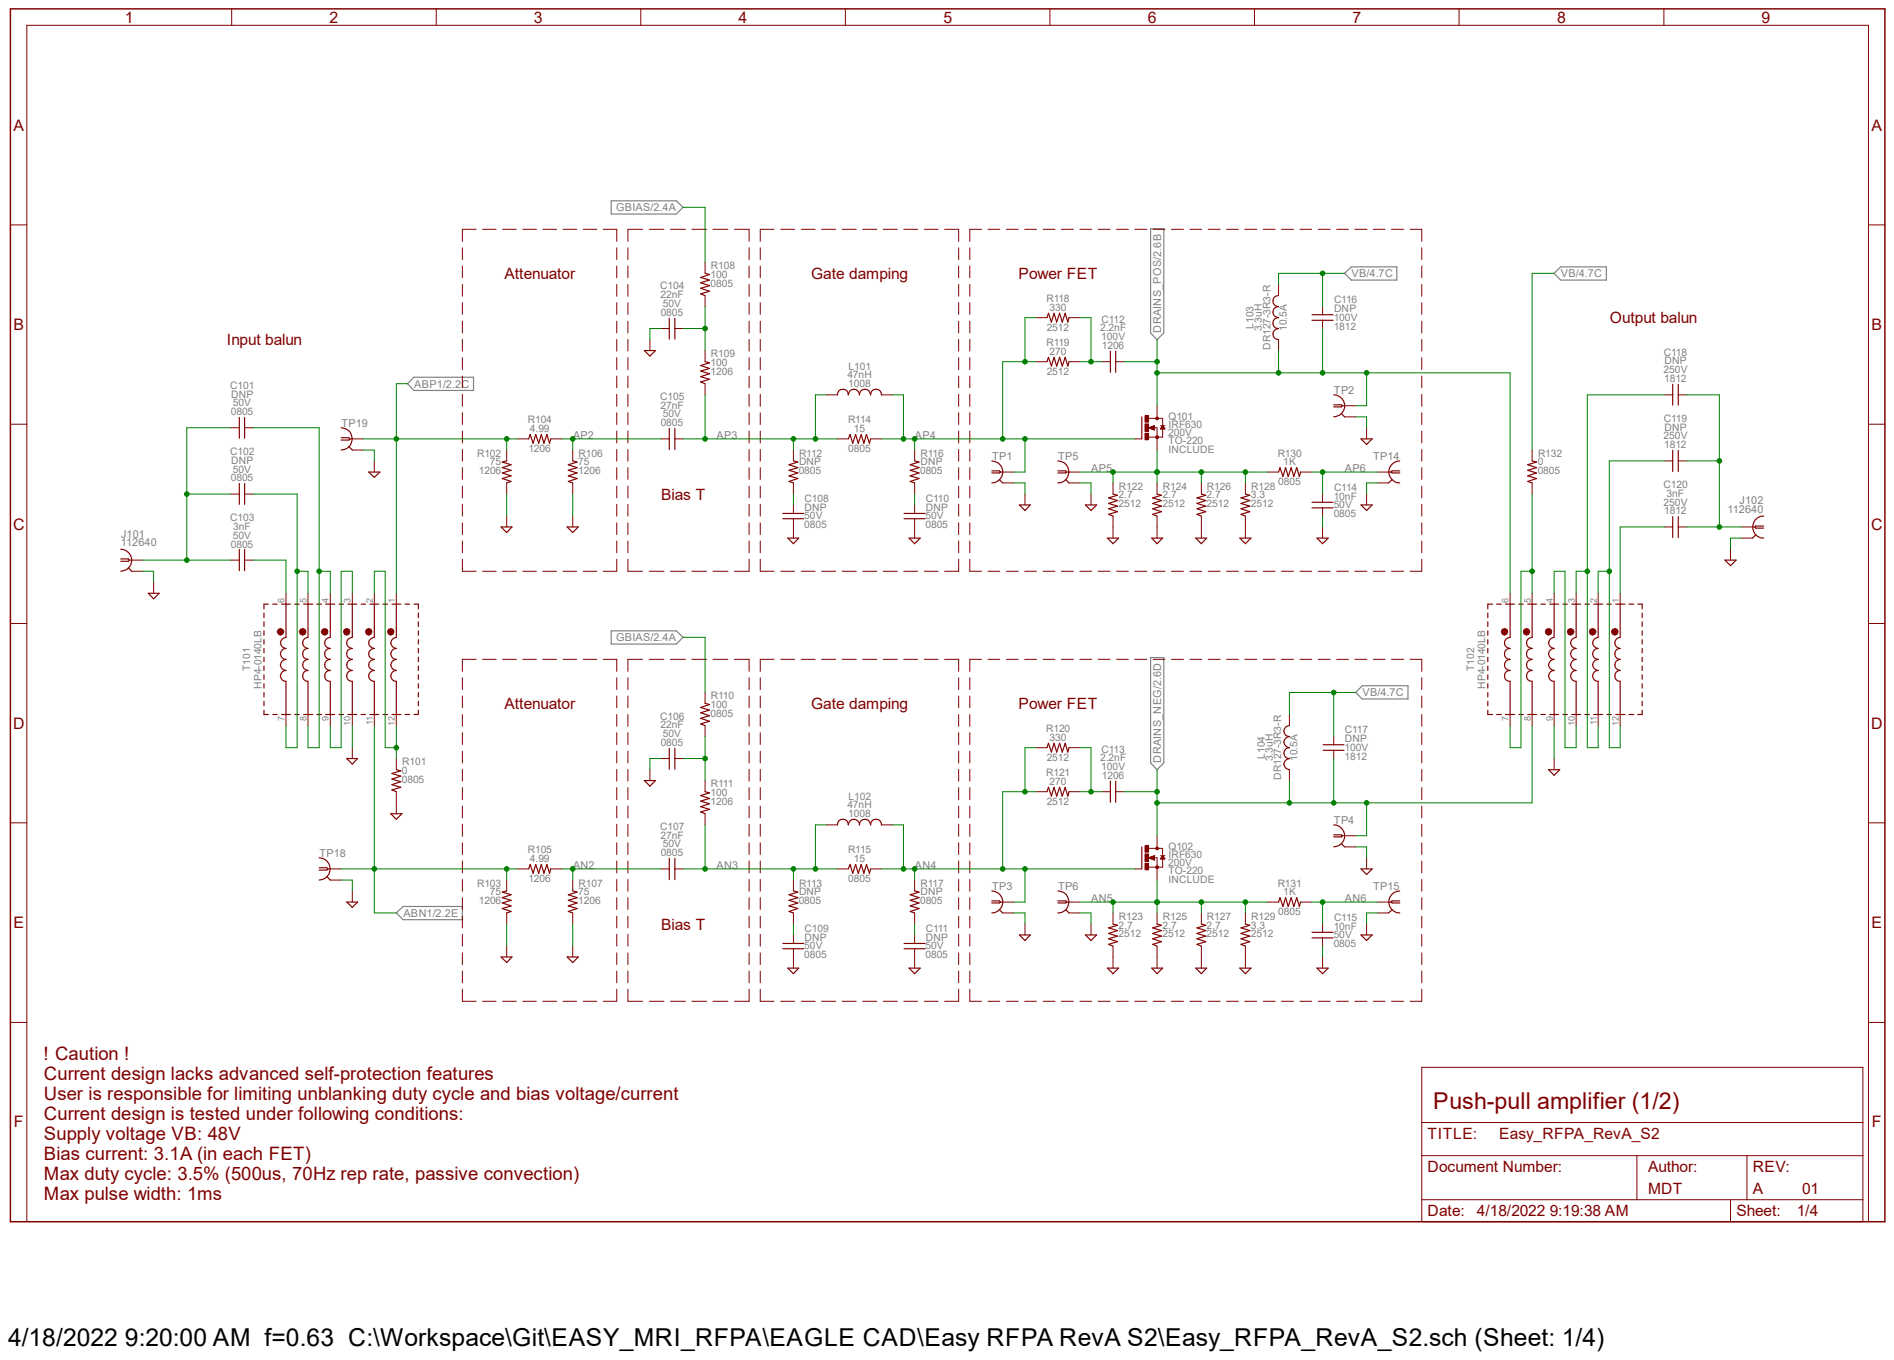
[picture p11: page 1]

! Caution !
Current design lacks advanced self-protection features
User is responsible for limiting unblanking duty cycle and bias voltage/current
Current design is tested under following conditions:
Supply voltage VB: 48V
Bias current: 3.1A (in each FET)
Max duty cycle: 3.5% (500us, 70Hz rep rate, passive convection)
Max pulse width: 1ms

Document Number: | Author: MDT | REV: 01 A

Date: 4/18/2022 9:19:38 AM | Sheet: 1/4

4/18/2022 9:20:00 AM f=0.63 C:\Workspace\Git\EASY_MRI_RFPA\EAGLE CAD\Easy RFPA RevA S2\Easy_RFPA_RevA_S2.sch (Sheet: 1/4)

# BN5 BN6 DRAINS_POS/1.6B

A

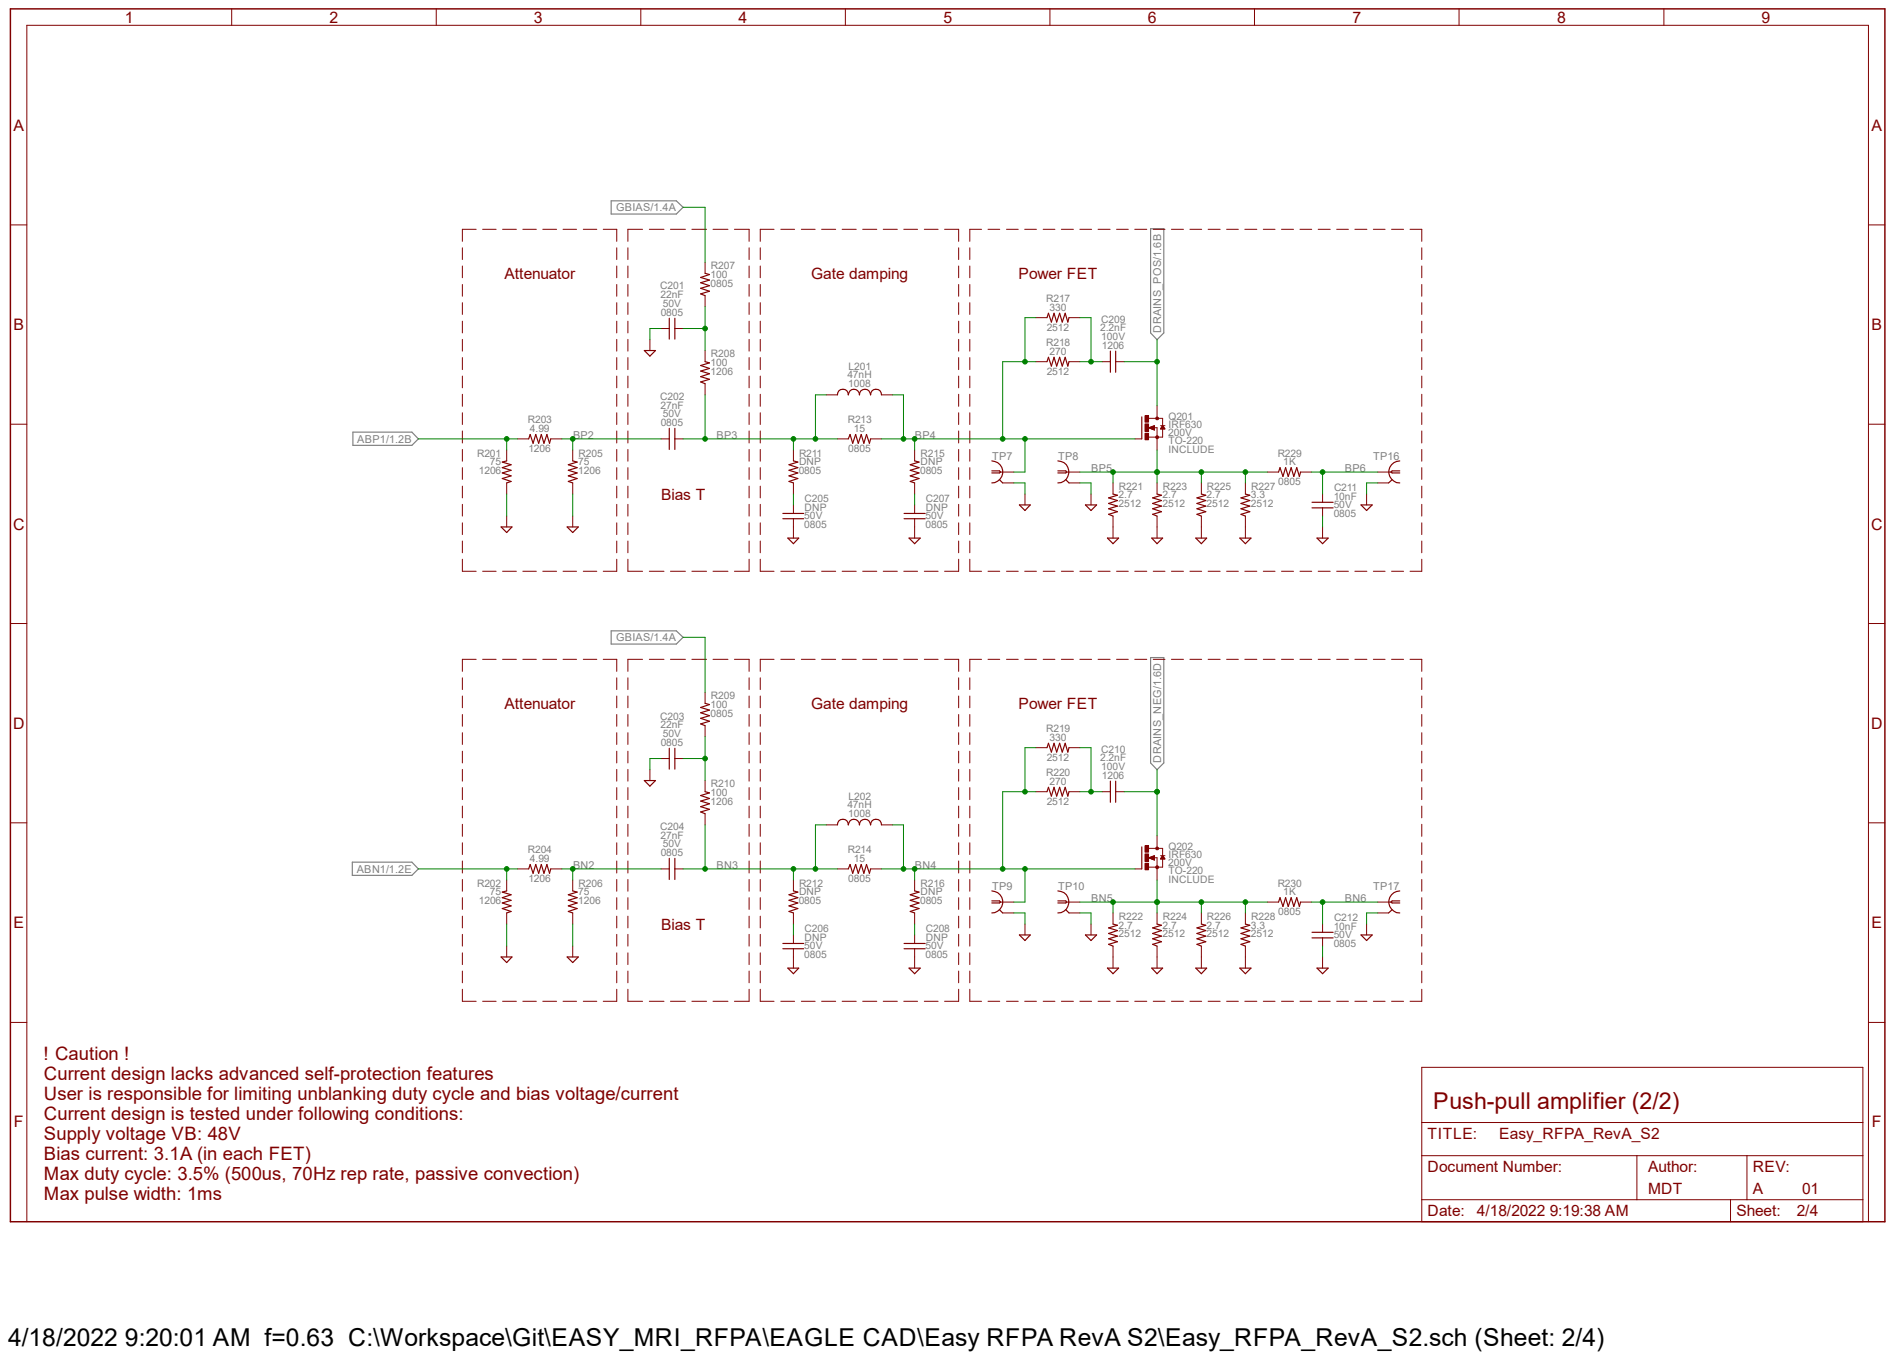
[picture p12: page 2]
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

Document Number: | Author: MDT | REV: 01 A

Date: 4/18/2022 9:19:38 AM | Sheet: 2/4

4/18/2022 9:20:01 AM f=0.63 C:\Workspace\Git\EASY_MRI_RFPA\EAGLE CAD\Easy RFPA RevA S2\Easy_RFPA_RevA_S2.sch (Sheet: 2/4)

If not using analog input,

A

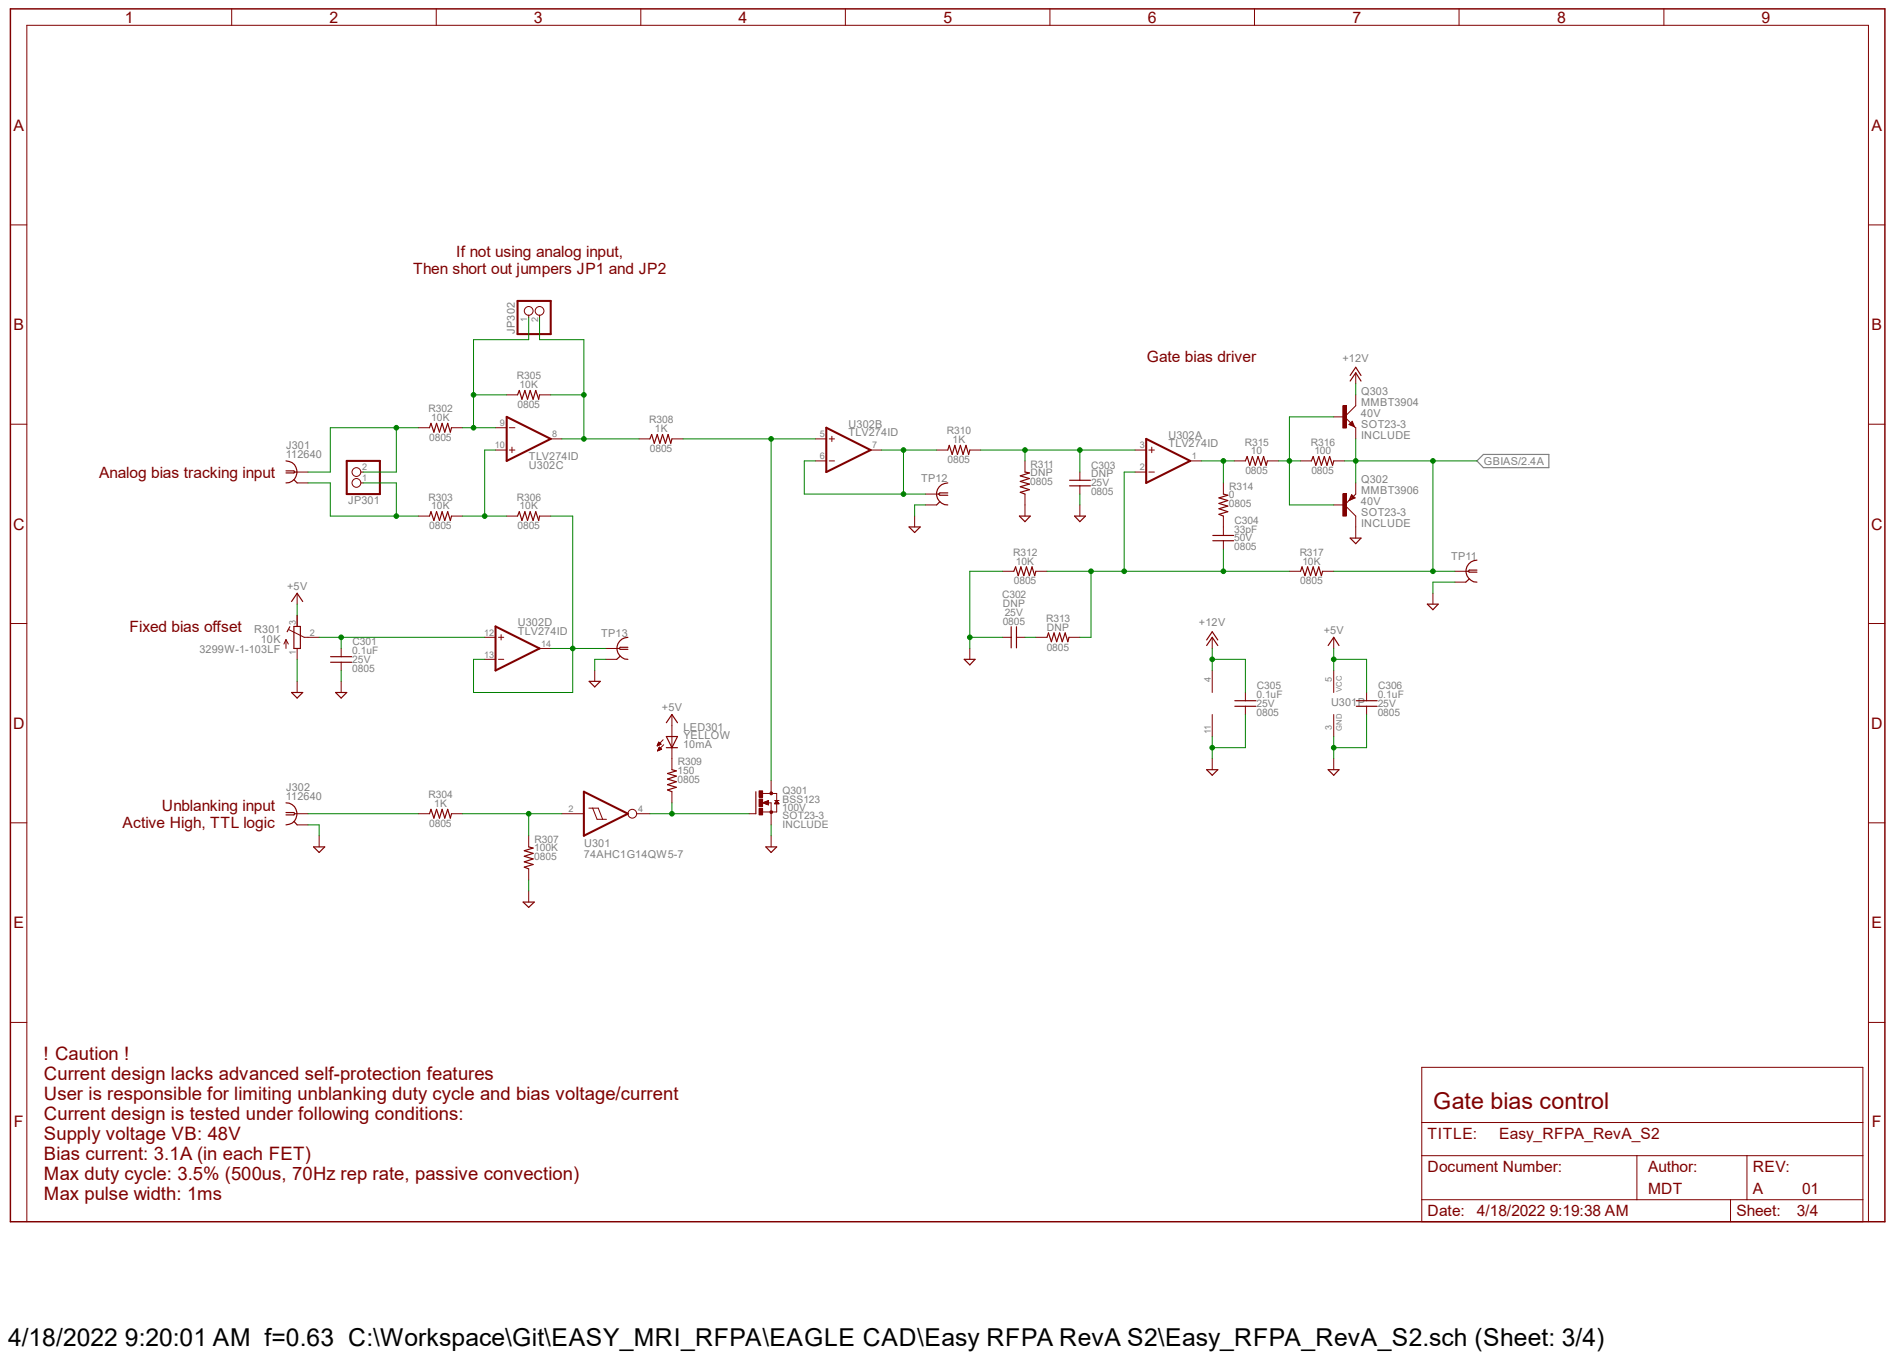
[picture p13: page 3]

Then short out jumpers JP1 and JP2

Analog bias tracking input

Unblanking input
Active High, TTL logic

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

Document Number: | Author: MDT | REV: 01 A

Date: 4/18/2022 9:19:38 AM | Sheet: 3/4

4/18/2022 9:20:01 AM f=0.63 C:\Workspace\Git\EASY_MRI_RFPA\EAGLE CAD\Easy RFPA RevA S2\Easy_RFPA_RevA_S2.sch (Sheet: 3/4)

A

A

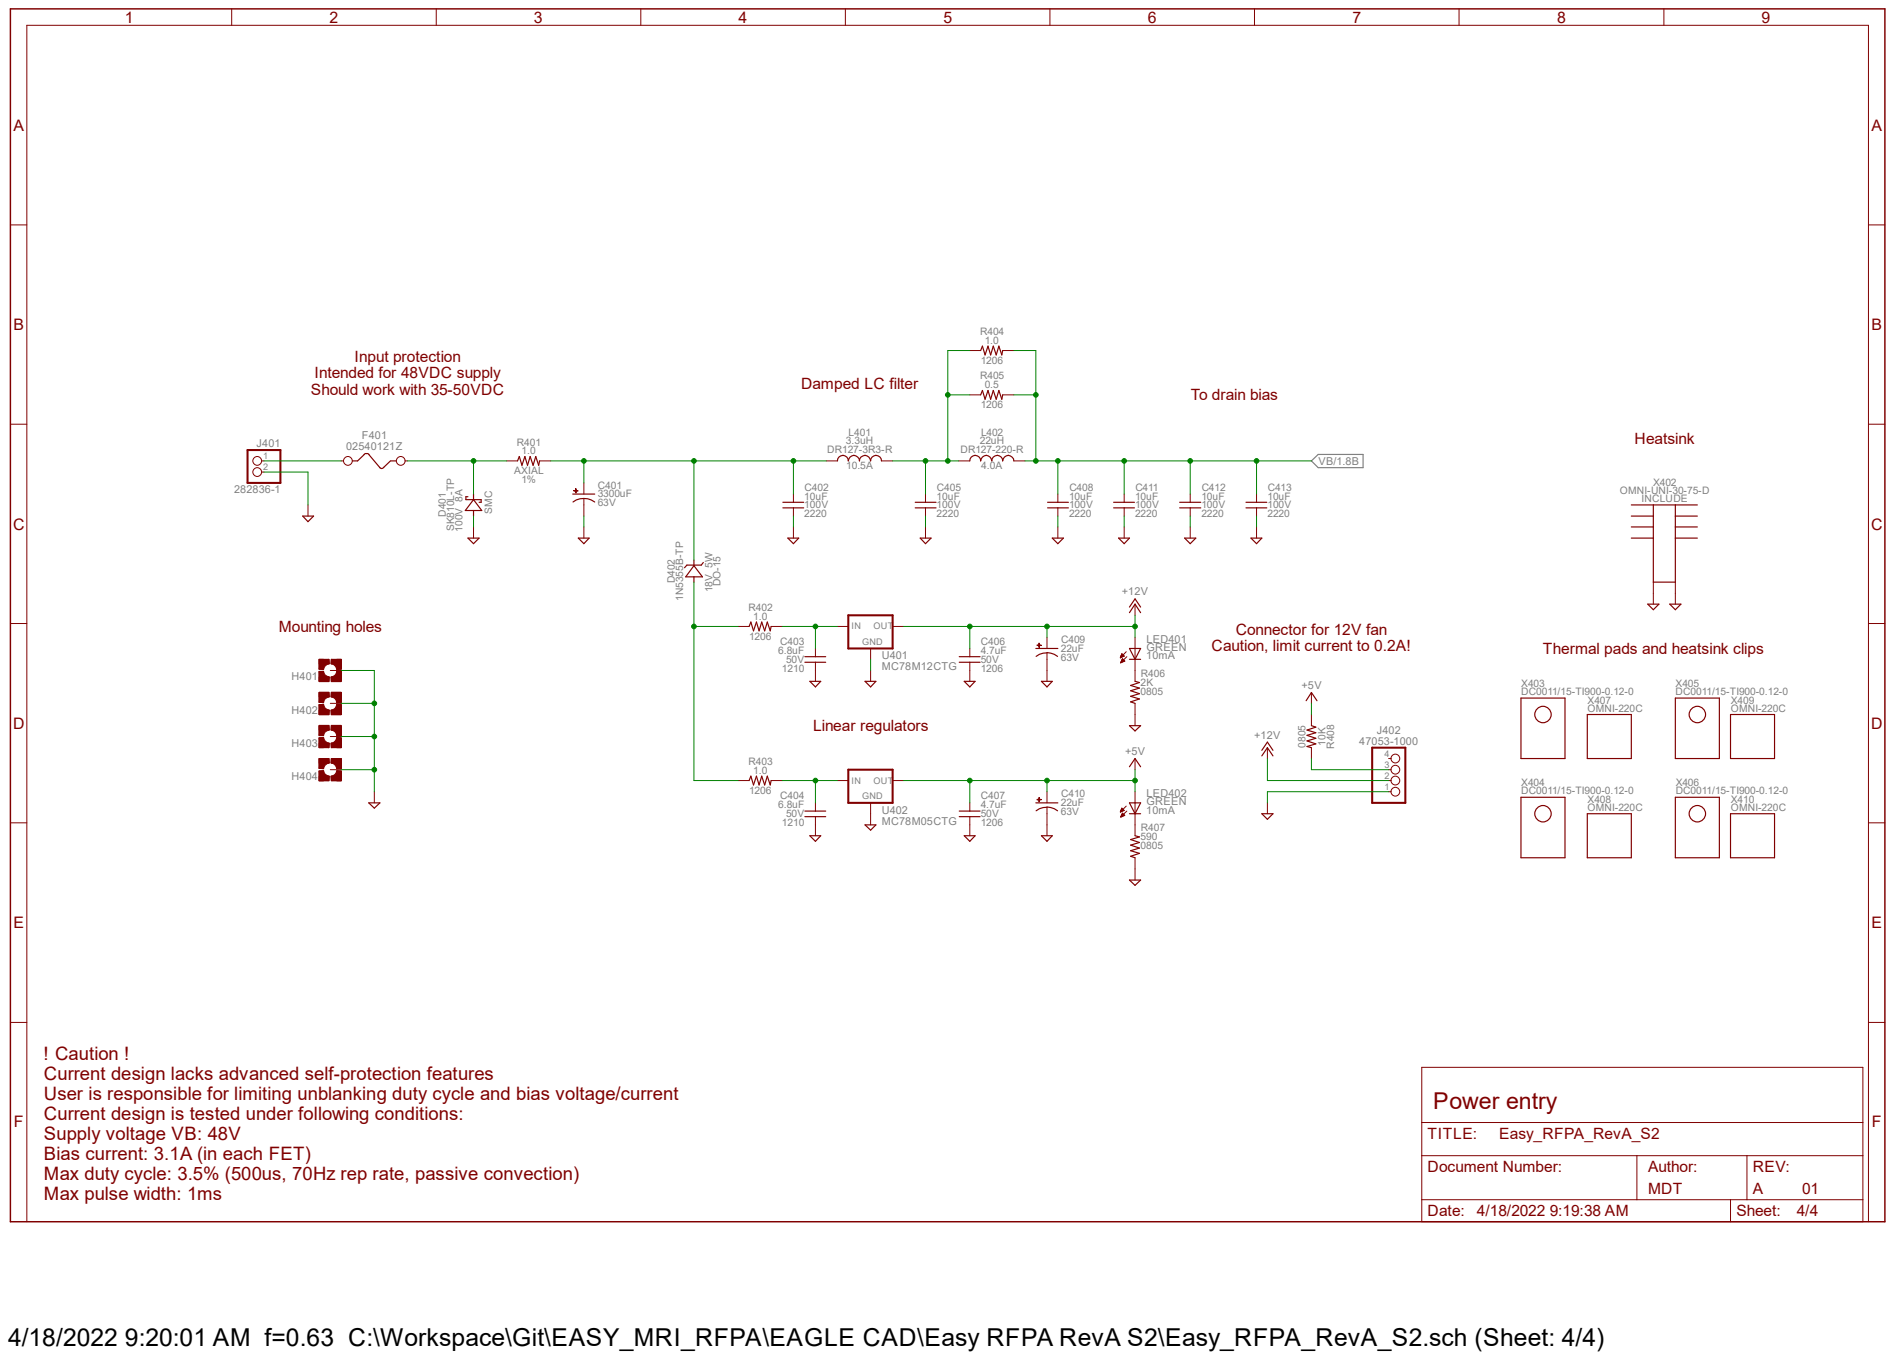
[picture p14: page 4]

Connector for 12V fan
Caution, limit current to 0.2A!

Thermal pads and heatsink clips

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

Document Number: | Author: MDT | REV:

Date: 4/18/2022 9:19:38 AM | Sheet: 4/4

4/18/2022 9:20:01 AM f=0.63 C:\Workspace\Git\EASY_MRI_RFPA\EAGLE CAD\Easy RFPA RevA S2\Easy_RFPA_RevA_S2.sch (Sheet: 4/4)

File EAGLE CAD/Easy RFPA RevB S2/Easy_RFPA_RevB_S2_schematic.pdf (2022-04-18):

A

A

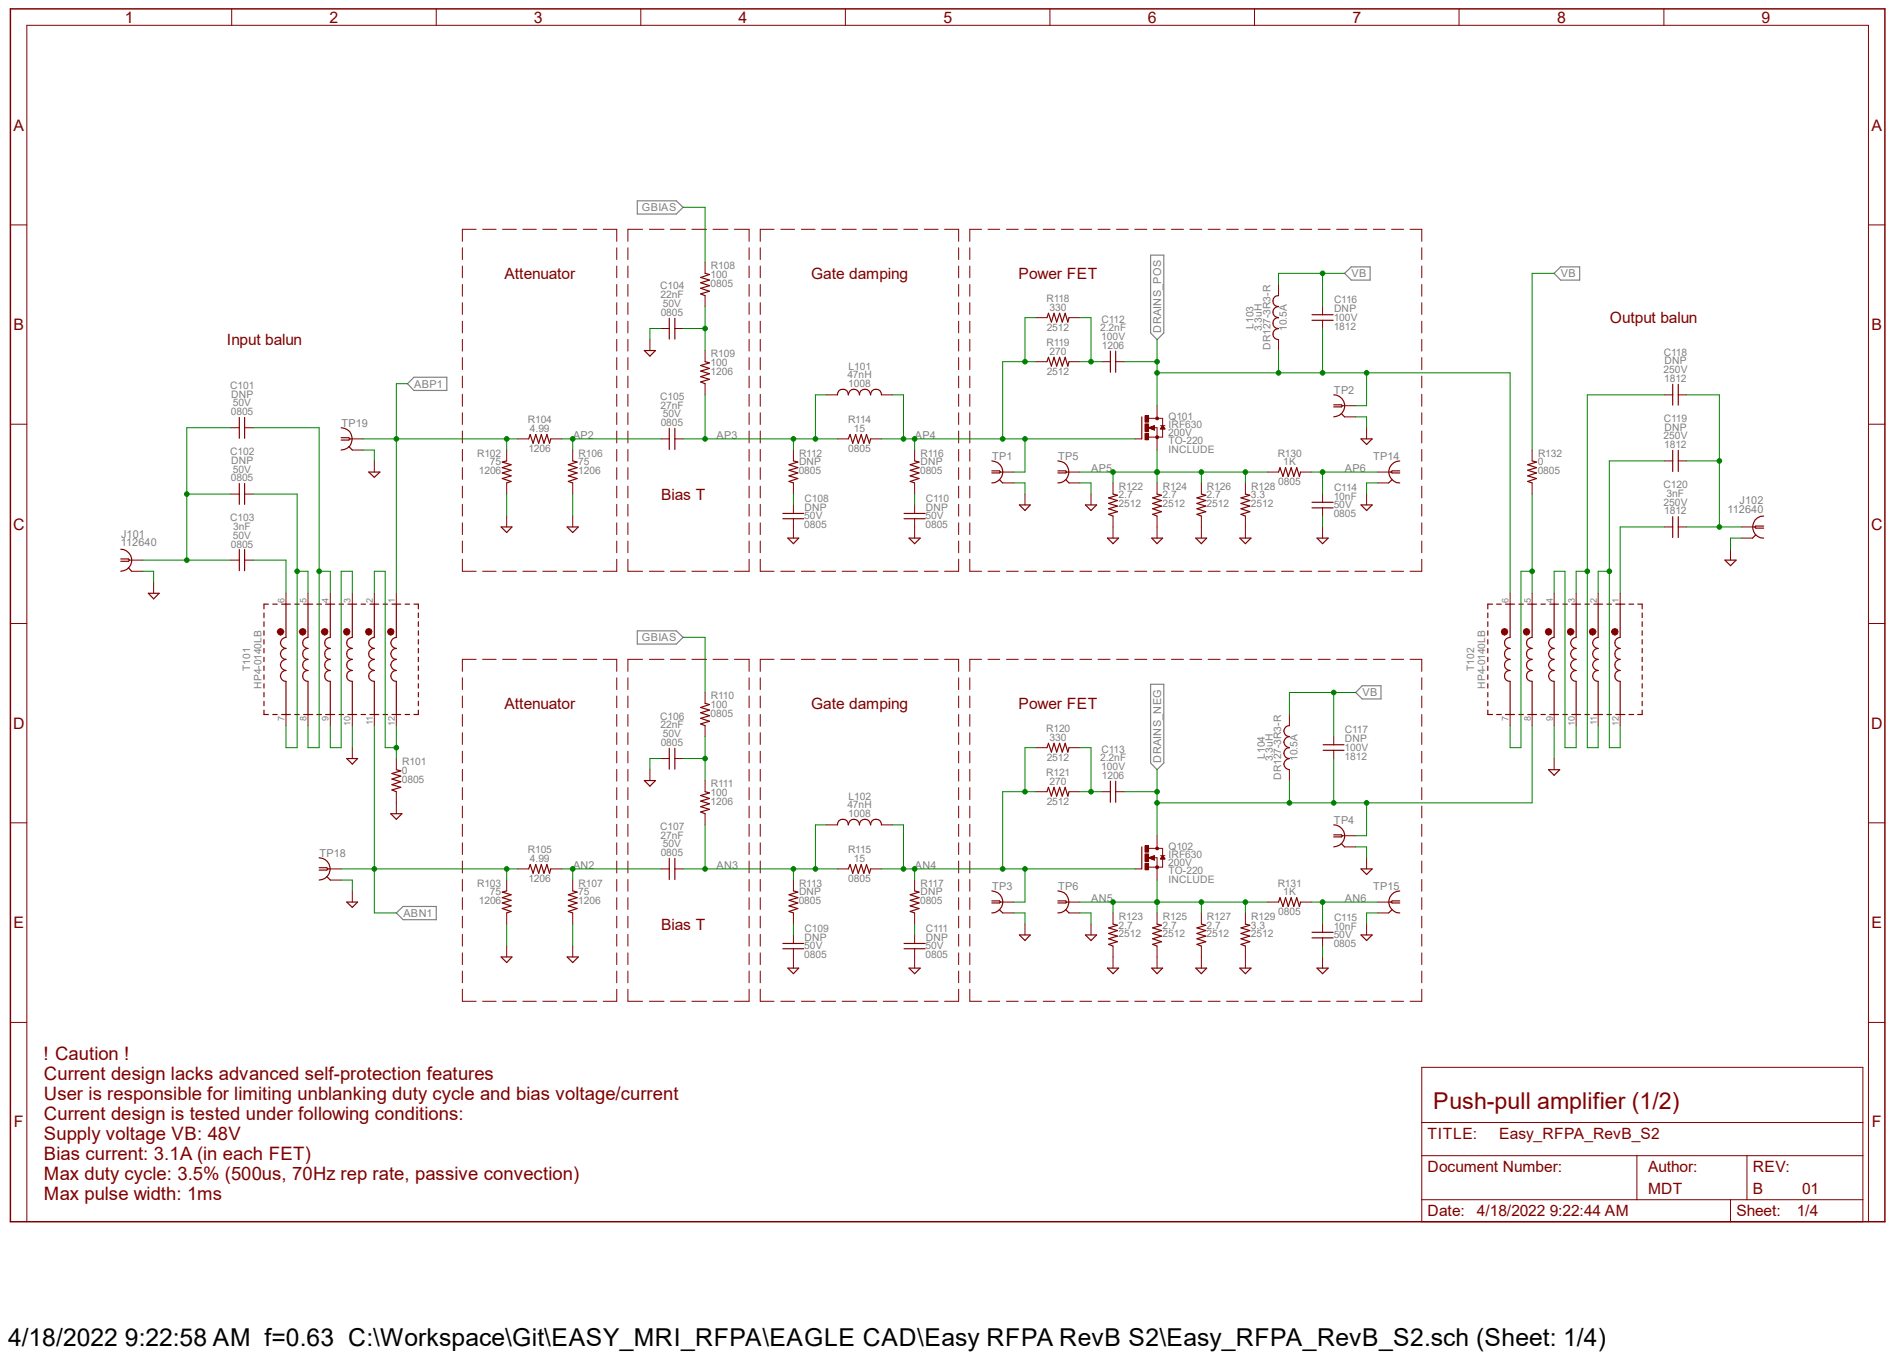
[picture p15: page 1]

! Caution !
Current design lacks advanced self-protection features
User is responsible for limiting unblanking duty cycle and bias voltage/current
Current design is tested under following conditions:
Supply voltage VB: 48V
Bias current: 3.1A (in each FET)
Max duty cycle: 3.5% (500us, 70Hz rep rate, passive convection)
Max pulse width: 1ms

Document Number: | Author: MDT | REV: 01 B

Date: 4/18/2022 9:22:44 AM | Sheet: 1/4

4/18/2022 9:22:58 AM f=0.63 C:\Workspace\Git\EASY_MRI_RFPA\EAGLE CAD\Easy RFPA RevB S2\Easy_RFPA_RevB_S2.sch (Sheet: 1/4)

A

A

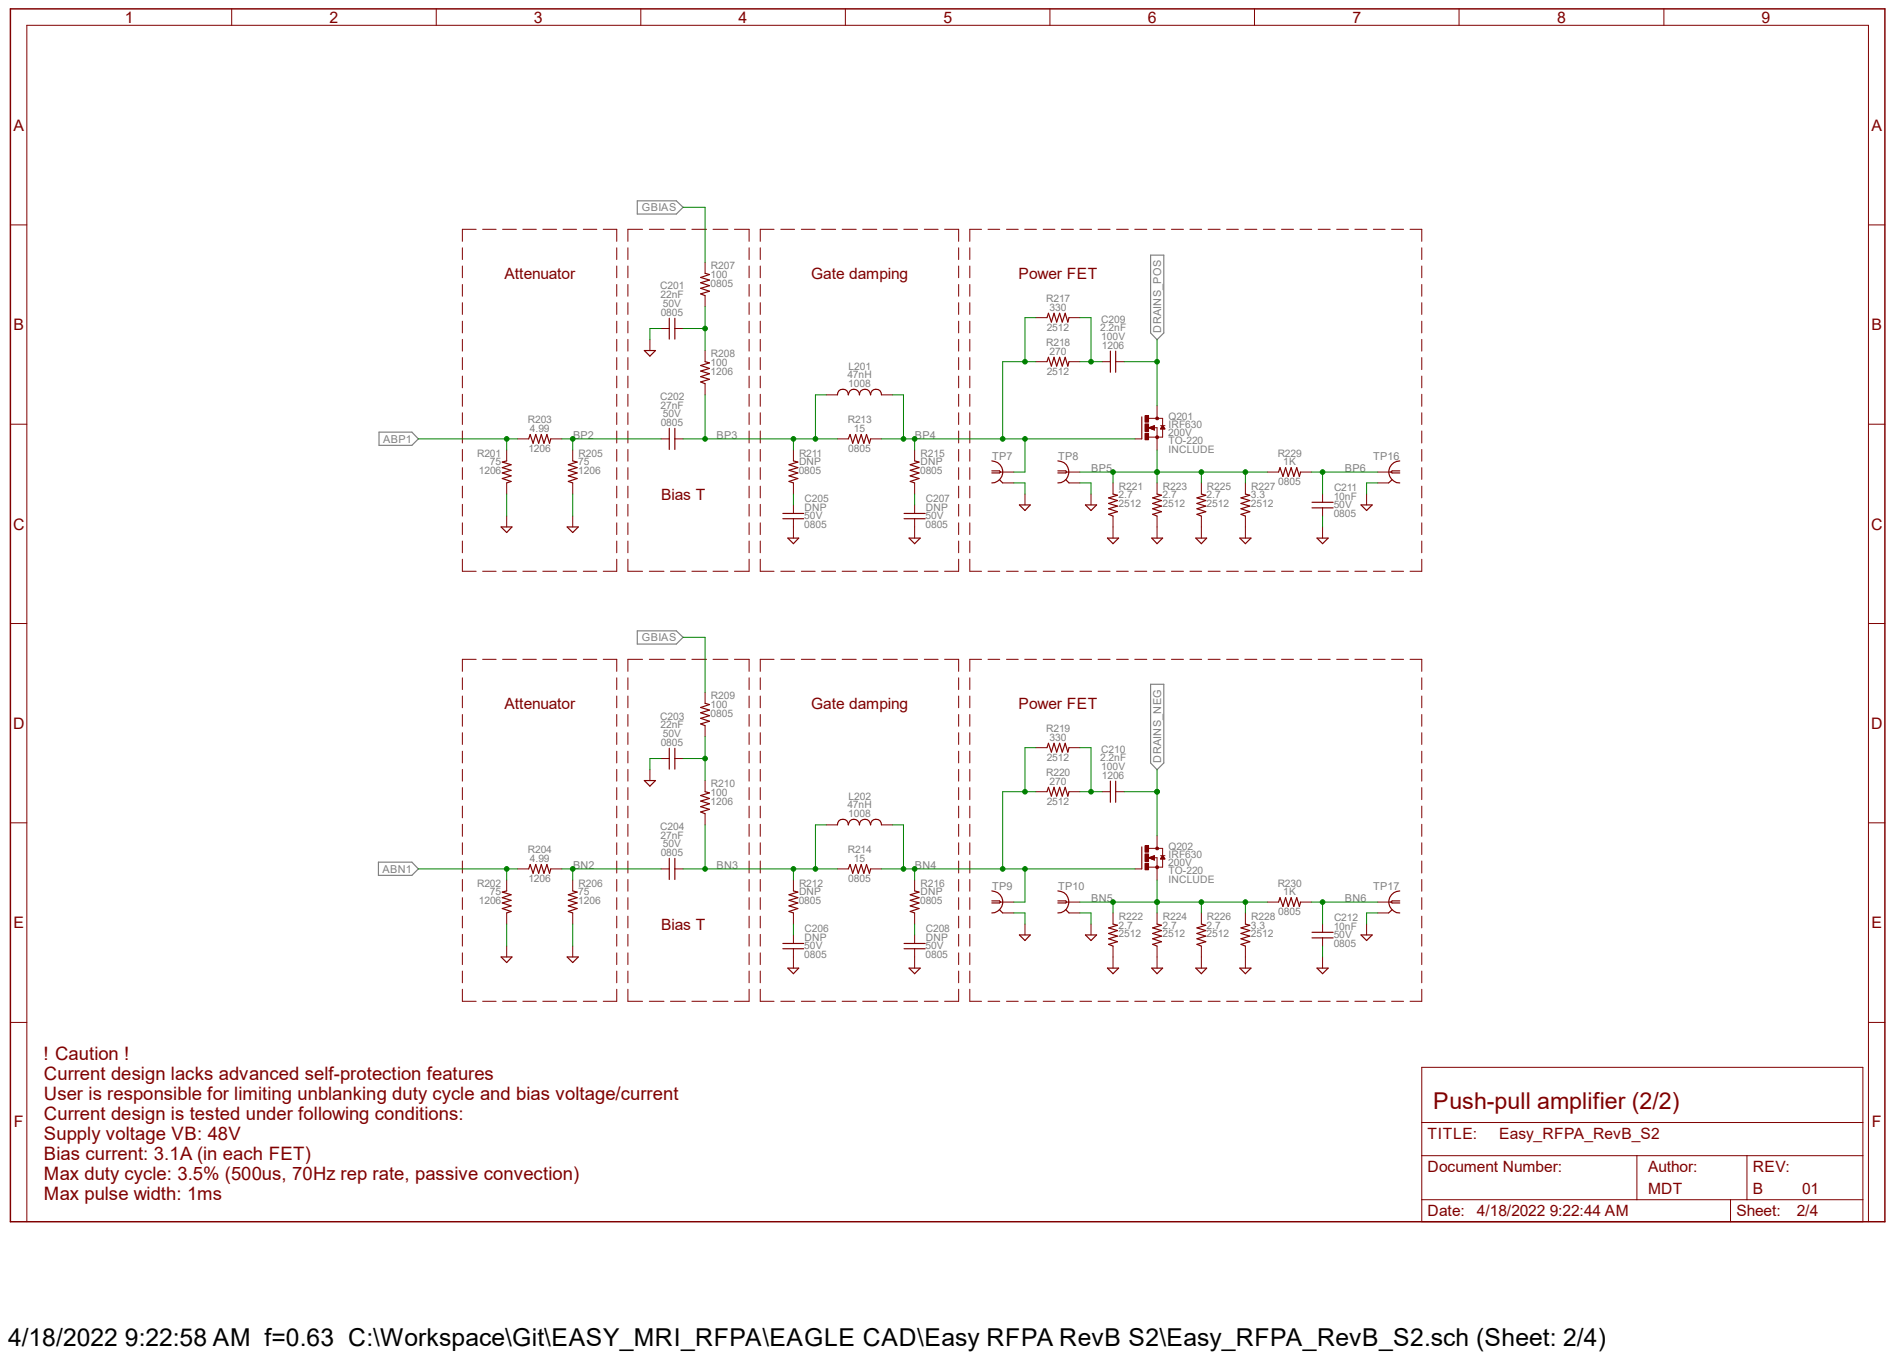
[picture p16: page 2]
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

Document Number: | Author: MDT | REV: 01 B

Date: 4/18/2022 9:22:44 AM | Sheet: 2/4

4/18/2022 9:22:58 AM f=0.63 C:\Workspace\Git\EASY_MRI_RFPA\EAGLE CAD\Easy RFPA RevB S2\Easy_RFPA_RevB_S2.sch (Sheet: 2/4)

If not using analog input,

A

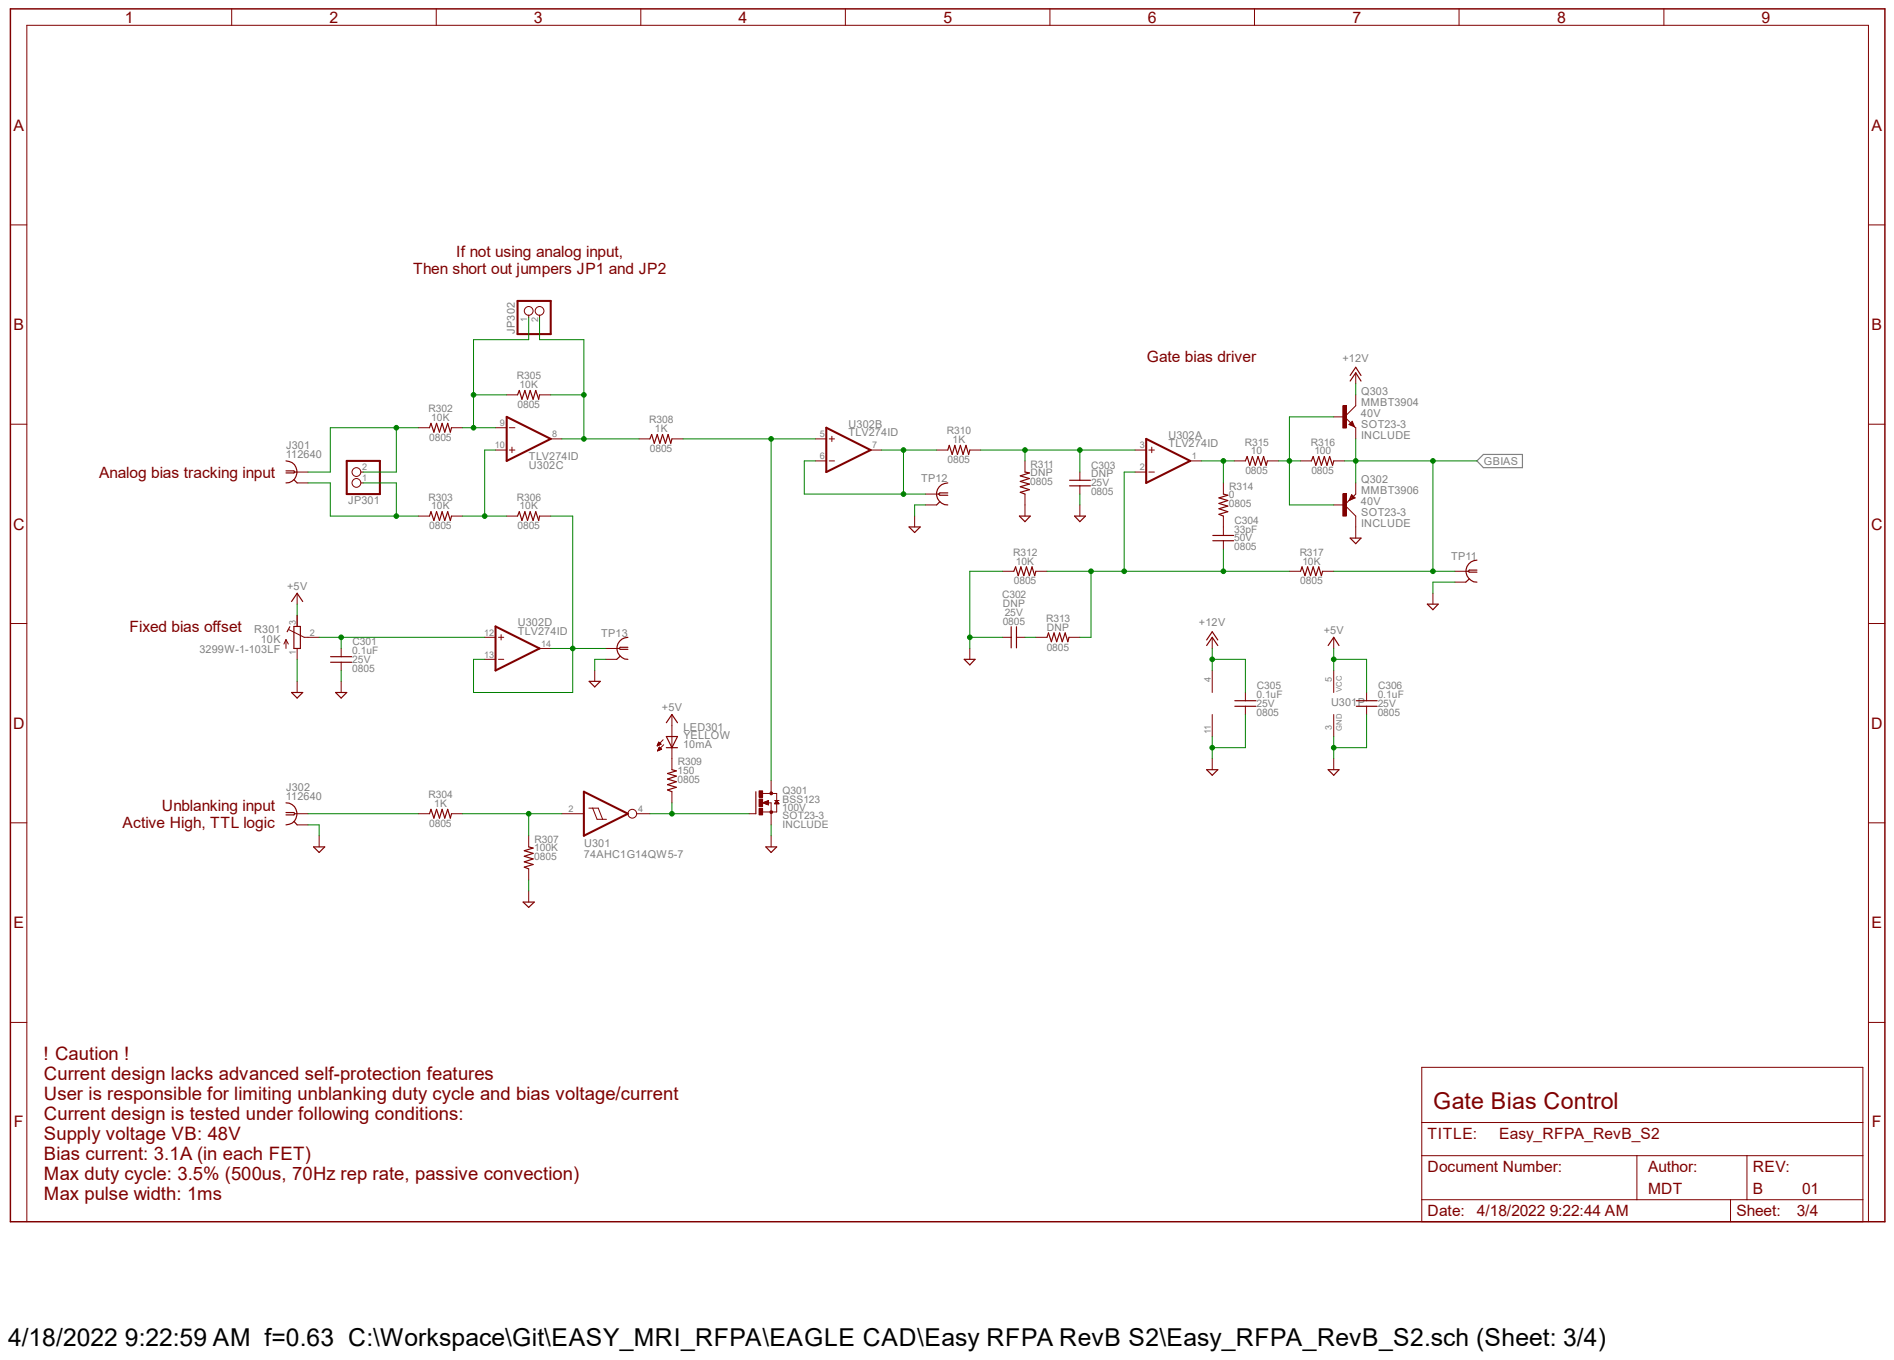
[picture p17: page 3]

Then short out jumpers JP1 and JP2

Analog bias tracking input

Unblanking input
Active High, TTL logic

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

Document Number: | Author: MDT | REV: 01 B

Date: 4/18/2022 9:22:44 AM | Sheet: 3/4

4/18/2022 9:22:59 AM f=0.63 C:\Workspace\Git\EASY_MRI_RFPA\EAGLE CAD\Easy RFPA RevB S2\Easy_RFPA_RevB_S2.sch (Sheet: 3/4)

A

A

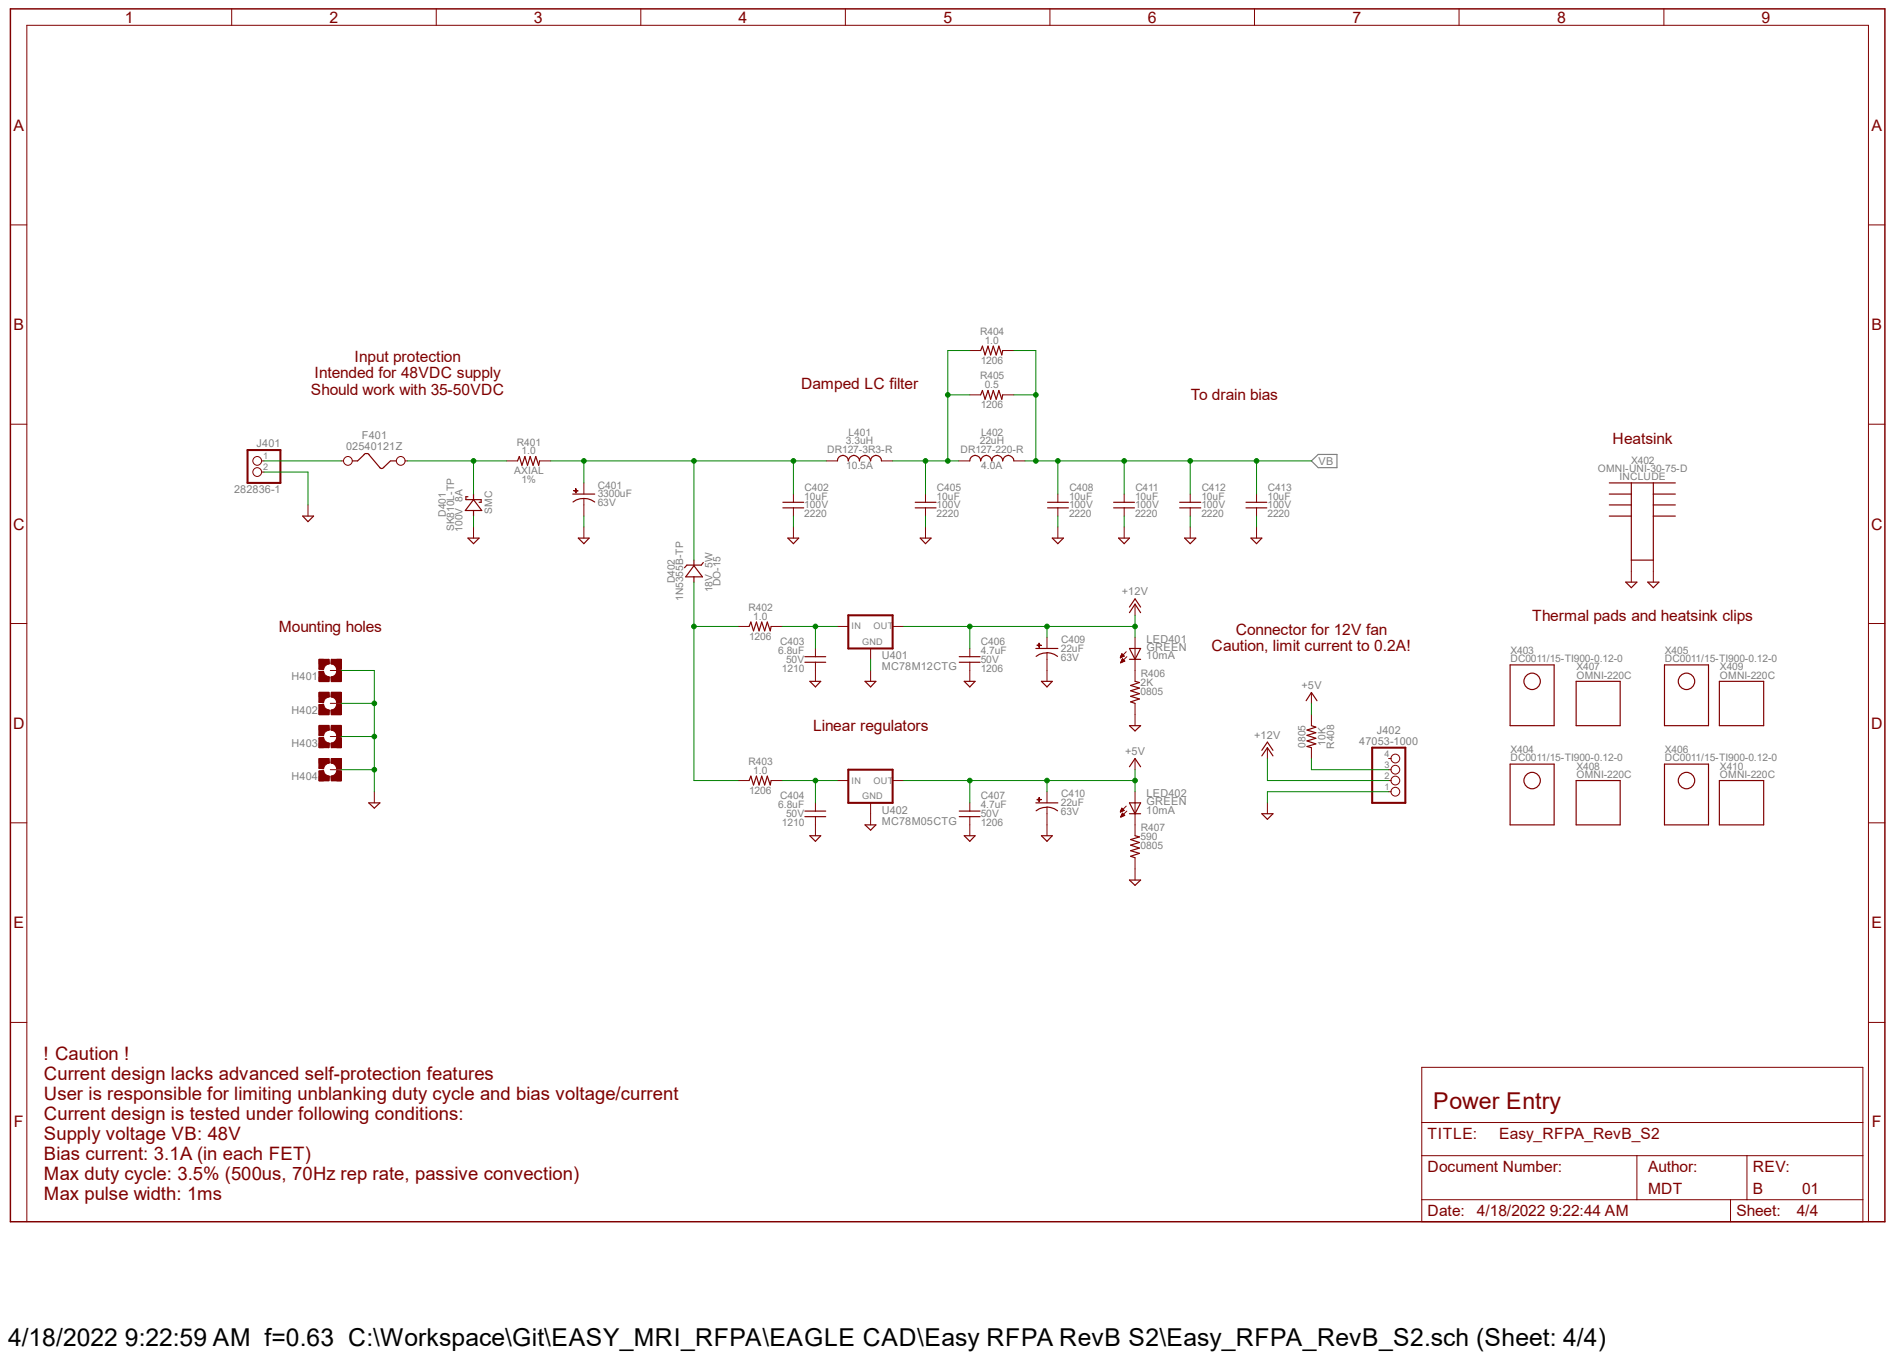
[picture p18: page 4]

Thermal pads and heatsink clips

Connector for 12V fan
Caution, limit current to 0.2A!

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

Document Number: | Author: MDT | REV:

Date: 4/18/2022 9:22:44 AM | Sheet: 4/4

4/18/2022 9:22:59 AM f=0.63 C:\Workspace\Git\EASY_MRI_RFPA\EAGLE CAD\Easy RFPA RevB S2\Easy_RFPA_RevB_S2.sch (Sheet: 4/4)

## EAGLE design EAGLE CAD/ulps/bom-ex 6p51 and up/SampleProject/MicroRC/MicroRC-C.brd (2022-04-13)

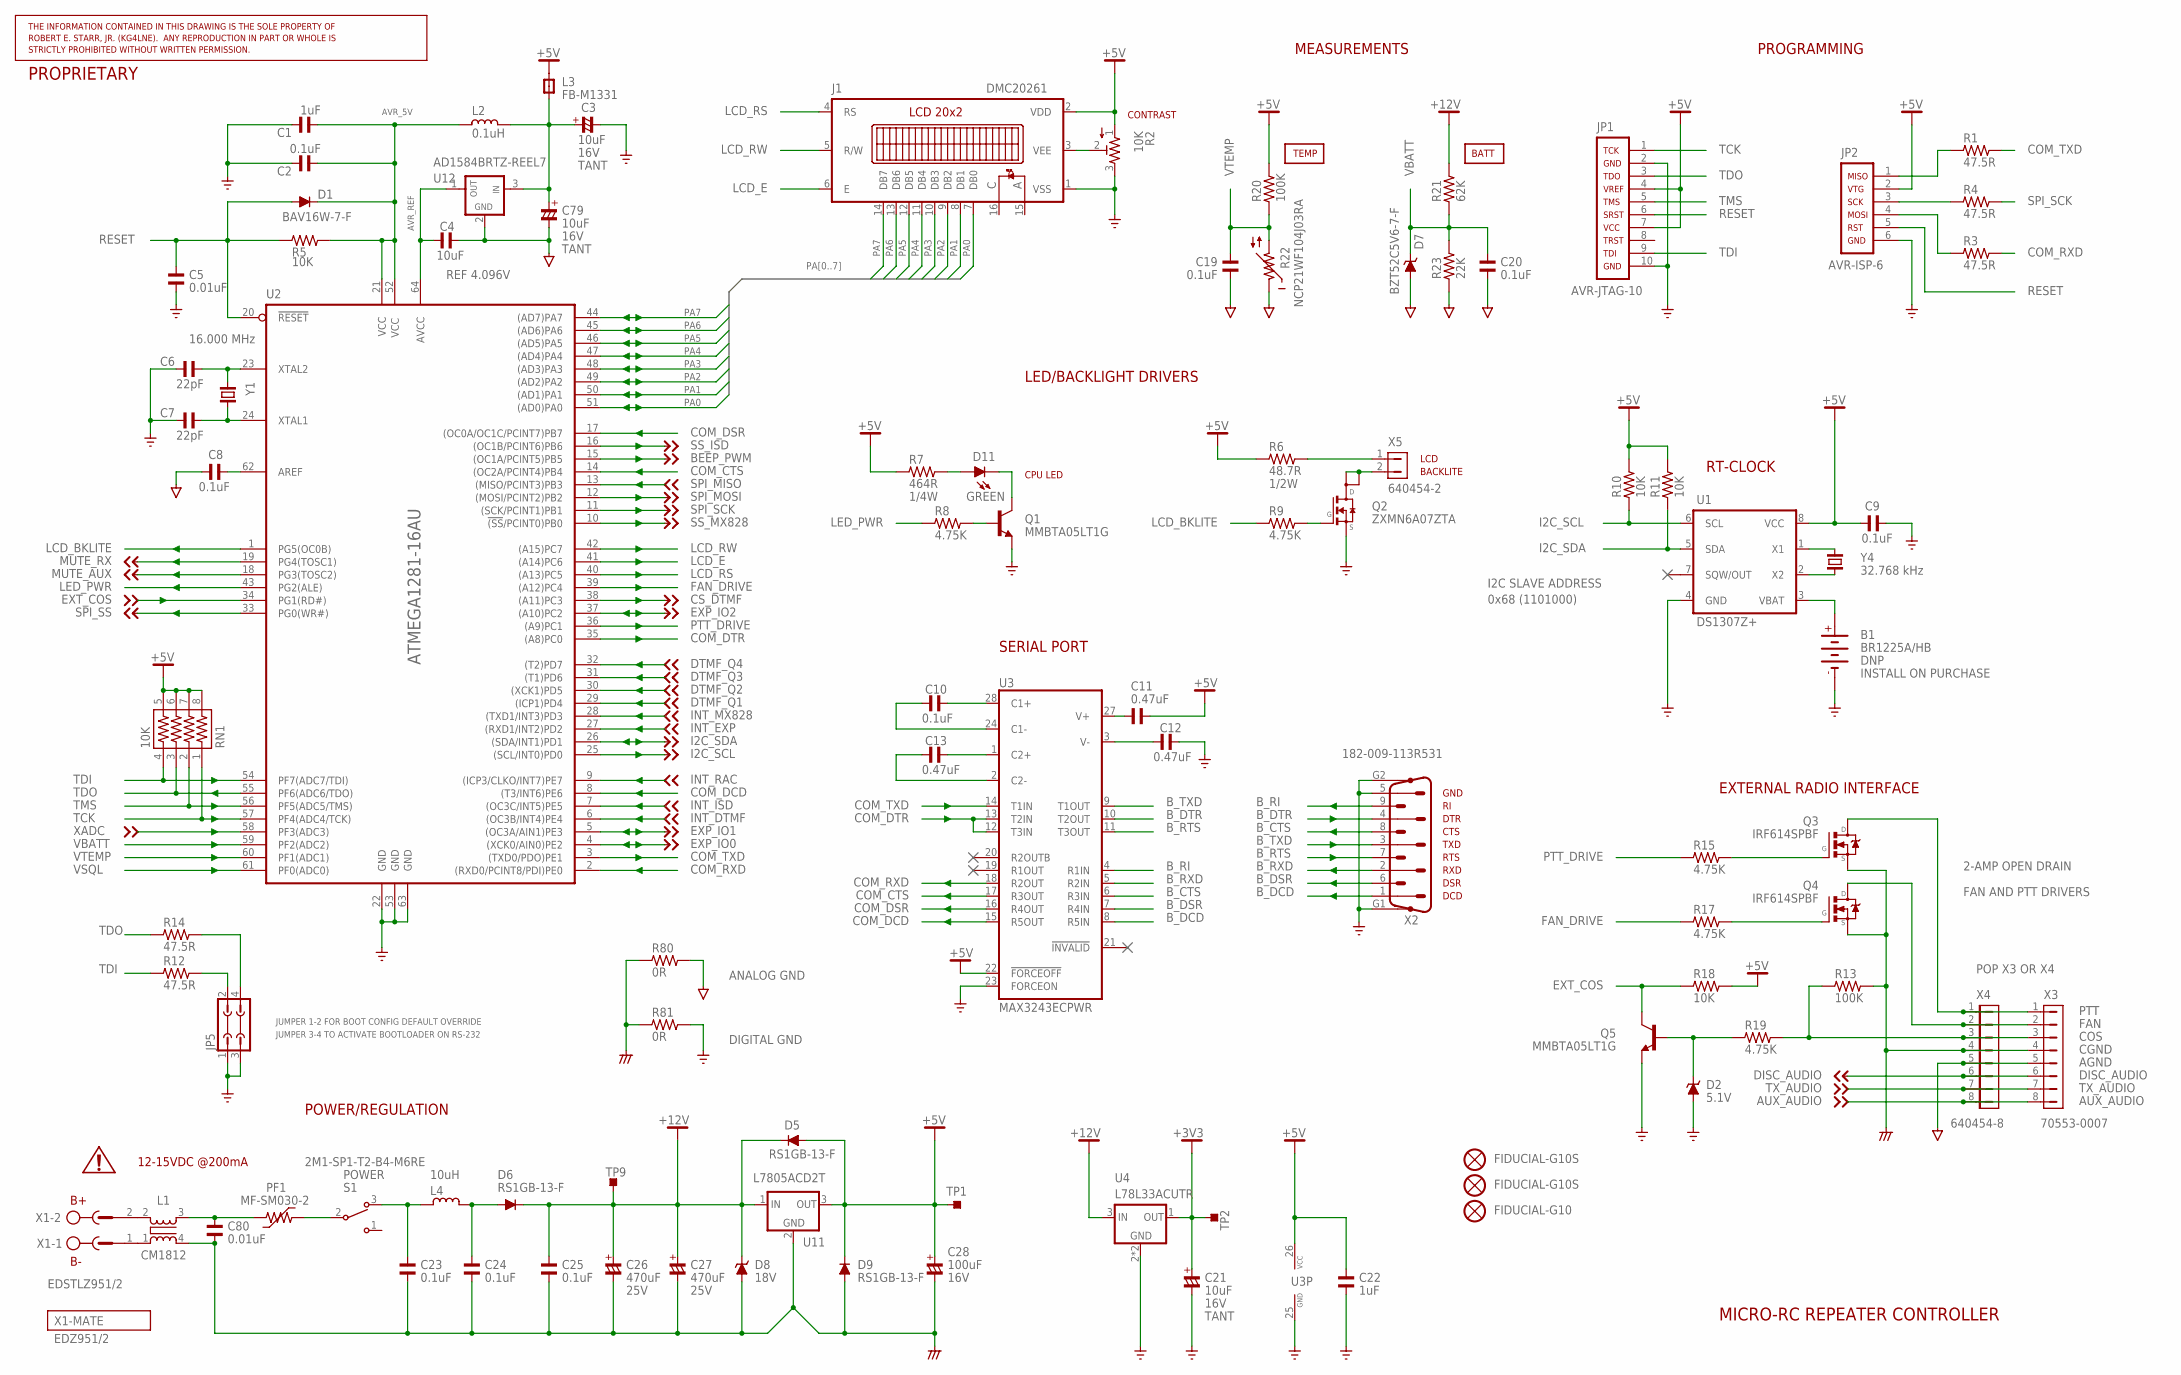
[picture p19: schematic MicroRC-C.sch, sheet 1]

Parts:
B1: BR1225A/HB; BR1225; PARTNO BR1225A/HB
C1, C22: 1uF; C0805; PARTNO C0805C105Z3VACTU
C2, C8, C9, C10, C19, C20: 0.1uF; C0805; PARTNO C0805F104K5RACTU
C3, C21, C79: 10uF; C3528/T; PARTNO T491B106M016AT
C4: 10uF; C0805; PARTNO C0805C106K9PACTU
C5: 0.01uF; C0805; PARTNO C0805C103K5RACTU
C6, C7: 22pF; C0805; PARTNO C0805C220J5GACTU
C11, C12, C13: 0.47uF; C0805; PARTNO C0805F474K3RACTU
C23, C24, C25: 0.1uF; C1206; PARTNO C1206C104K5RACTU
C26, C27: 470uF; CSV-G; PARTNO EEE-1EA471P
C28: 100uF; CSV-E/F; PARTNO EEE-1CA101P
C80: 0.01uF; C1206; PARTNO 12065C103KAT2A
D1: BAV16W-7-F; SOD123; PARTNO BAV16W-7-F
D2: 5.1V; SOD123; PARTNO BZT52C5V1-7-F
D5, D6, D9: RS1GB-13-F; SMB; PARTNO RS1GB-13-F
D7: BZT52C5V6-7-F; SOD123; PARTNO BZT52C5V6-7-F
D8: 18V; SMB; PARTNO 1SMB5931BT3G
D11: GREEN; LED535; PARTNO 5350T5
FIDUCIAL1, FIDUCIAL2: FIDUCIAL-G10S; G10S
FIDUCIAL3: FIDUCIAL-G10; G10
J1: DMC20261; PARTNO *
JP1: AVR-JTAG-10; PARTNO *
JP2: AVR-ISP-6
JP5: JP2Q; PARTNO *
L1: CM1812; PARTNO CM1812R600R-10
L2: 0.1uH; L1206; PARTNO PM1210-R10J
L3: FB-M1331; L1206; PARTNO PM2001-200
L4: 10uH; PM-13; PARTNO PM3308-100M
PF1: MF-SM030-2; SMD-7555; PARTNO MF-SM030-2
Q1, Q5: MMBTA05LT1G; SOT23; PARTNO MMBTA05LT1G
Q2: ZXMN6A07ZTA; SOT89; PARTNO ZXMN6A07ZTA
Q3, Q4: IRF614SPBF; D2PAK; PARTNO IRF614SPBF
R1, R3, R4, R12, R14: 47.5R; R0805; PARTNO ERJ-6ENF47R5V
R2: 10K; EVM-L4G; PARTNO EVM-L4GA00B14
R5, R10, R11, R18: 10K; R0805; PARTNO ERJ-6ENF1002V
R6: 48.7R; R2010; PARTNO ERJ-12SF48R7U
R7: 464R; R1210; PARTNO ERJ-14NF4640U
R8, R9, R15, R17, R19: 4.75K; R0805; PARTNO ERJ-6ENF4751V
R13, R20: 100K; R0805; PARTNO ERJ-6ENF1003V
R21: 62K; R0805; PARTNO ERJ-6ENF6192V
R22: NCP21WF104J03RA; R0805; PARTNO NCP21WF104J03RA
R23: 22K; R0805; PARTNO ERJ-6ENF2212V
R80, R81: 0R; R0805; PARTNO RC0805JR-070RL
RN1: 10K; 744-8; PARTNO 744C083103JPTR
S1: 2M1-SP1-T2-B4-M6RE; CK-A; PARTNO 2M1-SP1-T2-B4-M6RE
TP1, TP2, TP9: TPTP10SQ; TP10SQ
U1: DS1307Z+; SO08; PARTNO DS1307Z+
U2: ATMEGA1281-16AU; TQFP64-AEB; PARTNO ATMEGA1281-16AU
U3: MAX3243ECPWR; TSSOP28; PARTNO MAX3243ECPWR
U4: L78L33ACUTR; SOT89-4; PARTNO L78L33ACUTR
U11: L7805ACD2T; D2PAK; PARTNO L7805ACD2T
U12: AD1584BRTZ-REEL7; SOT23; PARTNO AD1584BRTZ-REEL7
X1: EDSTLZ951/2; 951-2; PARTNO EDSTLZ951/2
X2: 182-009-113R531; NC182M9; PARTNO 182-009-113R531
X3: 70553-0007; 70553-08; PARTNO 70553-0007
X4: 640454-8; MTA08-100; PARTNO 640454-8
X5: 640454-2; MTA-100-2V; PARTNO 640454-2
Y1: 16.000 MHz; TC38H; PARTNO ECS-160-18-9X
Y4: 32.768 kHz; TC26H; PARTNO ECS-.327-12.5-13X

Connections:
+3V3: C21.+, TP2.TP, U4.1 (OUT); also elsewhere on the board
+5V: C9.1, C11.1, C22.1, C28.+, D5.A, D9.C, J1.2 (VDD), JP1.4, JP1.7, JP2.2, L3.2, R2.1, R6.1, R7.1, R10.2, R11.2, R18.2, R20.2, RN1.5, RN1.6, RN1.7, RN1.8, TP1.TP, U1.8 (VCC), U3.22 (!FORCEOFF!), U3.26 (VCC), U11.3 (OUT); also elsewhere on the board
+12V: C25.1, C26.+, C27.+, D5.C, D6.C, D8.C, R21.2, TP9.TP, U4.3 (IN), U11.1 (IN); also elsewhere on the board
AGND: C4.1, C8.2, C19.2, C20.2, C79.-, D7.A, R22.1, R23.1, R80.2, U12.2 (GND), X3.5, X4.5; also elsewhere on the board
AUX_AUDIO: X3.8, X4.8; also elsewhere on the board
AVR_5V: C1.1, C2.1, D1.C, L2.2, R5.2, U2.21 (VCC), U2.52 (VCC1)
AVR_REF: C4.2, U2.64 (AVCC), U12.1 (OUT)
BEEP_PWM: U2.15 ((OC1A/PCINT5)PB5); also elsewhere on the board
B_CTS: U3.6 (R3IN), X2.8
B_DCD: U3.8 (R5IN), X2.1
B_DSR: U3.7 (R4IN), X2.6
B_DTR: U3.10 (T2OUT), X2.4
B_RI: U3.4 (R1IN), X2.9
B_RTS: U3.11 (T3OUT), X2.7
B_RXD: U3.5 (R2IN), X2.2
B_TXD: U3.9 (T1OUT), X2.3
CGND: C23.2, C24.2, C25.2, C26.-, C27.-, C28.-, C80.2, D8.A, D9.A, L1.4, Q3.3 (S), Q4.3 (S), R13.2, R80.1, R81.1, U11.2 (GND), X3.4, X4.4
COM_CTS: U2.14 ((OC2A/PCINT4)PB4), U3.17 (R3OUT)
COM_DCD: U2.8 ((T3/INT6)PE6), U3.15 (R5OUT)
COM_DSR: U2.17 ((OC0A/OC1C/PCINT7)PB7), U3.16 (R4OUT)
COM_DTR: U2.35 ((A8)PC0), U3.12 (T3IN), U3.13 (T2IN)
COM_RXD: R3.2, U2.2 ((RXD0/PCINT8/PDI)PE0), U3.18 (R2OUT)
COM_TXD: R1.2, U2.3 ((TXD0/PDO)PE1), U3.14 (T1IN)
COS: R13.1, R19.2, X3.3, X4.3
CS_DTMF: U2.38 ((A11)PC3); also elsewhere on the board
DISC_AUDIO: X3.6, X4.6; also elsewhere on the board
DTMF_Q1: U2.29 ((ICP1)PD4); also elsewhere on the board
DTMF_Q2: U2.30 ((XCK1)PD5); also elsewhere on the board
DTMF_Q3: U2.31 ((T1)PD6); also elsewhere on the board
DTMF_Q4: U2.32 ((T2)PD7); also elsewhere on the board
EXP_IO0: U2.4 ((XCK0/AIN0)PE2); also elsewhere on the board
EXP_IO1: U2.5 ((OC3A/AIN1)PE3); also elsewhere on the board
EXP_IO2: U2.37 ((A10)PC2); also elsewhere on the board
EXT_COS: Q5.3 (C), R18.1, U2.34 (PG1(RD#))
FAN: Q4.2 (D), X3.2, X4.2
FAN_DRIVE: R17.1, U2.39 ((A12)PC4)
GND: B1.-, C1.2, C2.2, C3.-, C5.2, C6.2, C7.2, C9.2, C12.1, C21.-, C22.2, D2.A, J1.1 (VSS), JP1.2, JP1.10, JP2.6, JP5.1, JP5.3, Q1.2 (E), Q2.3 (S), Q5.2 (E), R2.3, R81.2, U1.4 (GND), U2.22 (GND), U2.53 (GND1), U2.63 (GND2), U3.23 (FORCEON), U3.25 (GND), U4.2 (GND), U4.4 (GND), X2.5, X2.G1, X2.G2; also elsewhere on the board
I2C_SCL: R10.1, U1.6 (SCL), U2.25 ((SCL/INT0)PD0); also elsewhere on the board
I2C_SDA: R11.1, U1.5 (SDA), U2.26 ((SDA/INT1)PD1); also elsewhere on the board
INT_DTMF: U2.6 ((OC3B/INT4)PE4); also elsewhere on the board
INT_EXP: U2.27 ((RXD1/INT2)PD2); also elsewhere on the board
INT_ISD: U2.7 ((OC3C/INT5)PE5); also elsewhere on the board
INT_MX828: U2.28 ((TXD1/INT3)PD3); also elsewhere on the board
INT_RAC: U2.9 ((ICP3/CLKO/INT7)PE7); also elsewhere on the board
LCD_BKLITE: R9.1, U2.1 (PG5(OC0B))
LCD_E: J1.6 (E), U2.41 ((A14)PC6)
LCD_RS: J1.4 (RS), U2.40 ((A13)PC5)
LCD_RW: J1.5 (R/W), U2.42 ((A15)PC7)
LED_PWR: R8.1, U2.43 (PG2(ALE))
MUTE_AUX: U2.18 (PG3(TOSC2)); also elsewhere on the board
MUTE_RX: U2.19 (PG4(TOSC1)); also elsewhere on the board
unnamed: L1.1, X1.1
unnamed: C8.1, U2.62 (AREF)
unnamed: JP5.2, R12.2
unnamed: C23.1, L4.1, S1.3 (O)
unnamed: L1.2, X1.2
unnamed: C24.1, D6.A, L4.2
unnamed: U1.1 (X1), Y4.2
unnamed: U1.2 (X2), Y4.1
unnamed: C7.1, U2.24 (XTAL1), Y1.1
unnamed: JP5.4, R14.2
unnamed: C12.2, U3.3 (V-)
unnamed: C11.2, U3.27 (V+)
unnamed: C6.1, U2.23 (XTAL2), Y1.2
unnamed: C13.1, U3.1 (C2+)
unnamed: C10.1, U3.28 (C1+)
unnamed: C13.2, U3.2 (C2-)
unnamed: C10.2, U3.24 (C1-)
unnamed: B1.+, U1.3 (VBAT)
unnamed: Q3.1 (G), R15.2
unnamed: Q2.1 (G), R9.2
unnamed: Q2.2 (D), Q2.4 (D2), X5.2
unnamed: R6.2, X5.1
unnamed: D2.C, Q5.1 (B), R19.1
unnamed: PF1.2, S1.2
unnamed: Q4.1 (G), R17.2
unnamed: C80.1, L1.3, PF1.1
unnamed: C3.+, C79.+, L2.1, L3.1, U12.3 (IN)
unnamed: D11.K (C), Q1.3 (C)
unnamed: D11.A, R7.2
unnamed: Q1.1 (B), R8.2
unnamed: JP2.1, R1.1
unnamed: JP2.3, R4.1
unnamed: JP2.4, R3.1
PA0: J1.7 (DB0), U2.51 ((AD0)PA0)
PA1: J1.8 (DB1), U2.50 ((AD1)PA1)
PA2: J1.9 (DB2), U2.49 ((AD2)PA2)
PA3: J1.10 (DB3), U2.48 ((AD3)PA3)
PA4: J1.11 (DB4), U2.47 ((AD4)PA4)
PA5: J1.12 (DB5), U2.46 ((AD5)PA5)
PA6: J1.13 (DB6), U2.45 ((AD6)PA6)
PA7: J1.14 (DB7), U2.44 ((AD7)PA7)
PTT: Q3.2 (D), X3.1, X4.1
PTT_DRIVE: R15.1, U2.36 ((A9)PC1)
RESET: C5.1, D1.A, JP1.6, JP2.5, R5.1, U2.20 (!RESET!)
SPI_MISO: U2.13 ((MISO/PCINT3)PB3); also elsewhere on the board
SPI_MOSI: U2.12 ((MOSI/PCINT2)PB2); also elsewhere on the board
SPI_SCK: R4.2, U2.11 ((SCK/PCINT1)PB1); also elsewhere on the board
SPI_SS: U2.33 (PG0(WR#)); also elsewhere on the board
SS_ISD: U2.16 ((OC1B/PCINT6)PB6); also elsewhere on the board
SS_MX828: U2.10 (!(SS!/PCINT0)PB0); also elsewhere on the board
TCK: JP1.1, RN1.1, U2.57 (PF4(ADC4/TCK))
TDI: JP1.9, R12.1, RN1.4, U2.54 (PF7(ADC7/TDI))
TDO: JP1.3, R14.1, RN1.3, U2.55 (PF6(ADC6/TDO))
TMS: JP1.5, RN1.2, U2.56 (PF5(ADC5/TMS))
TX_AUDIO: X3.7, X4.7; also elsewhere on the board
VBATT: C20.1, D7.C, R21.1, R23.2, U2.59 (PF2(ADC2))
VEE_LCD: J1.3 (VEE), R2.2
VSQL: U2.61 (PF0(ADC0)); also elsewhere on the board
VTEMP: C19.1, R20.1, R22.2, U2.60 (PF1(ADC1))
XADC: U2.58 (PF3(ADC3)); also elsewhere on the board

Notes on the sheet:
MICRO-RC REPEATER CONTROLLER
BATT
TEMP
CONTRAST
BACKLITE
LCD
RT-CLOCK
SERIAL PORT
DCD
CPU LED
DSR
RXD
RTS
TXD
CTS
DTR
GND
MEASUREMENTS
POWER/REGULATION
EXTERNAL RADIO INTERFACE
LED/BACKLIGHT DRIVERS
PROGRAMMING
12-15VDC @200mA
POWER
ANALOG GND
DIGITAL GND
2-AMP OPEN DRAIN
FAN AND PTT DRIVERS
REF 4.096V
JUMPER 1-2 FOR BOOT CONFIG DEFAULT OVERRIDE
JUMPER 3-4 TO ACTIVATE BOOTLOADER ON RS-232
I2C SLAVE ADDRESS
0x68 (1101000)

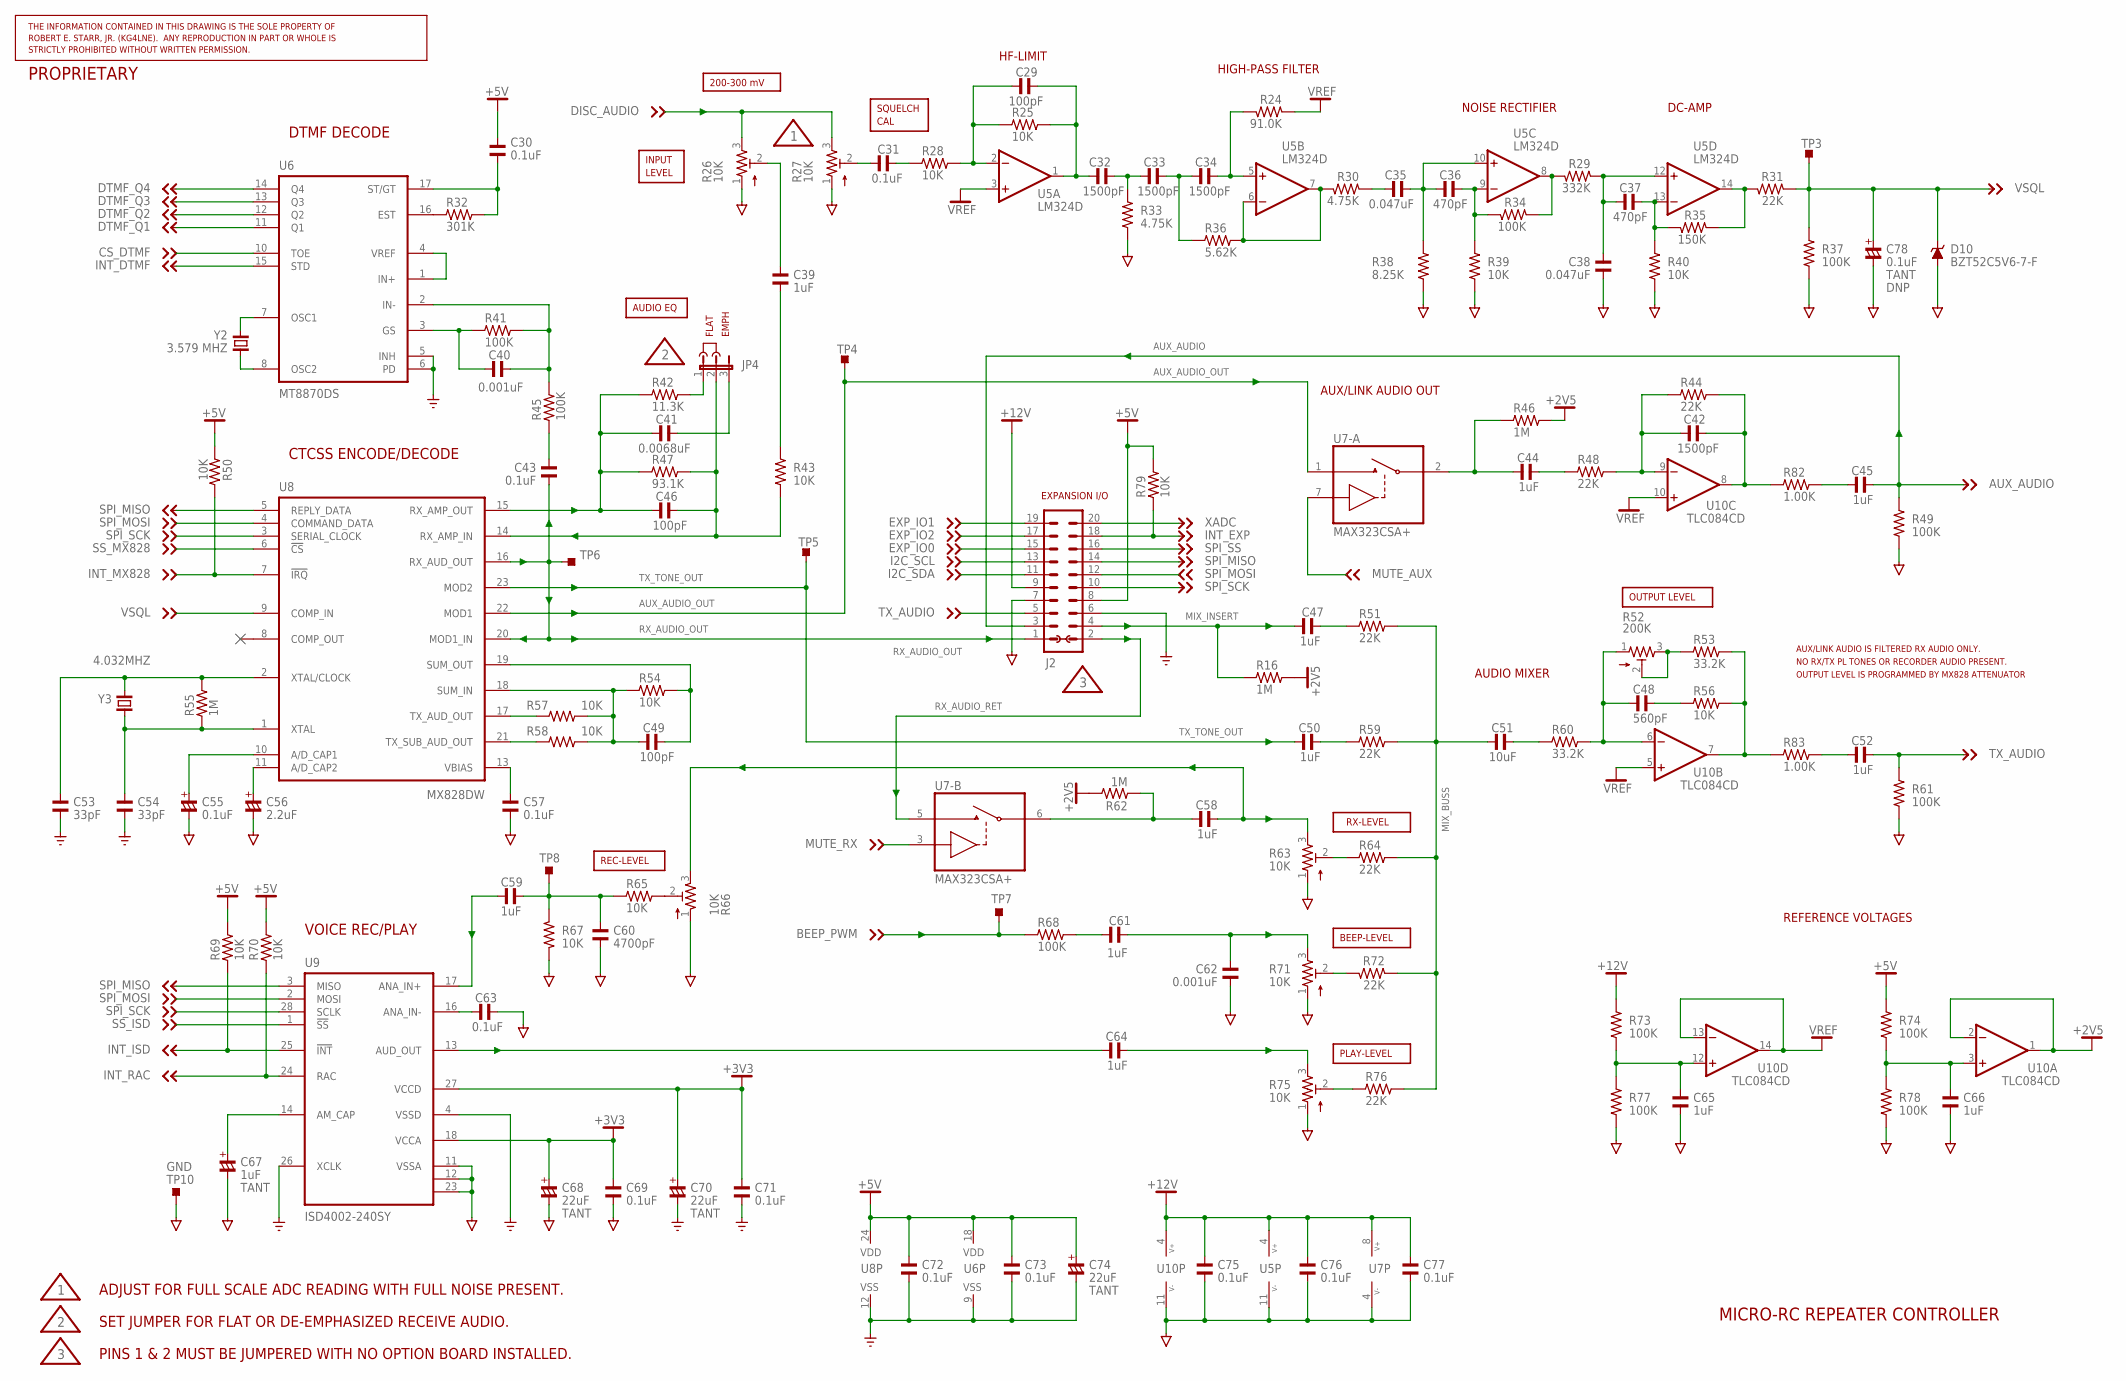
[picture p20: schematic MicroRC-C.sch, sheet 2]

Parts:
C29, C46, C49: 100pF; C0805; PARTNO C0805C101J5GACTU
C30, C31, C43, C57, C63, C69, C71, C72, C73, C75, C76, C77: 0.1uF; C0805; PARTNO C0805F104K5RACTU
C32, C33, C34, C42: 1500pF; C0805; PARTNO C0805C152K5RACTU
C35, C38: 0.047uF; C0805; PARTNO C0805C473K5RACTU
C36, C37: 470pF; C0805; PARTNO C0805C471J5GACTU
C39, C44, C45, C47, C50, C52, C58, C59, C61, C64, C65, C66: 1uF; C0805; PARTNO C0805C105Z3VACTU
C40, C62: 0.001uF; C0805; PARTNO C0805C102K5RACTU
C41: 0.0068uF; C0805; PARTNO C0805C682K5RACTU
C48: 560pF; C0805; PARTNO C0805C561J5GACTU
C51: 10uF; C0805; PARTNO C0805C106K9PACTU
C53, C54: 33pF; C0805; PARTNO C0805C330J5GACTU
C55: 0.1uF; C3216/T; PARTNO T491A104K035AT
C56: 2.2uF; C3216/T; PARTNO T491A225K010AT
C60: 4700pF; C0805; PARTNO C0805C472K5RACTU
C67: 1uF; C3216/T; PARTNO T491A105K016AT
C68, C70, C74: 22uF; C3528/T; PARTNO T491B226M016AT
C78: 0.1uF; C3216/T; PARTNO DNP
D10: BZT52C5V6-7-F; SOD123; PARTNO BZT52C5V6-7-F
J2: MA10-2; PARTNO *
JP4: JP2E; JP2; PARTNO *
R16, R46, R55, R62: 1M; R0805; PARTNO ERJ-6ENF1004V
R24: 91.0K; R0805; PARTNO ERJ-6ENF9092V
R25, R28, R39, R40, R43, R50, R54, R56, R57, R58, R65, R67, R69, R70, R79: 10K; R0805; PARTNO ERJ-6ENF1002V
R26, R27, R63, R71, R75: 10K; EVME-SIDE; PARTNO EVM-EGGA00B14
R29: 332K; R0805; PARTNO ERJ-6ENF3323V
R30, R33: 4.75K; R0805; PARTNO ERJ-6ENF4751V
R31, R44, R48, R51, R59, R64, R72, R76: 22K; R0805; PARTNO ERJ-6ENF2212V
R32: 301K; R0805; PARTNO ERJ-6ENF3013V
R34, R37, R41, R45, R49, R61, R68, R73, R74, R77, R78: 100K; R0805; PARTNO ERJ-6ENF1003V
R35: 150K; R0805; PARTNO ERJ-6ENF1503V
R36: 5.62K; R0805; PARTNO ERJ-6ENF5621V
R38: 8.25K; R0805; PARTNO ERJ-6ENF8251V
R42: 11.3K; R0805; PARTNO ERJ-6ENF1132V
R47: 93.1K; R0805; PARTNO ERJ-6ENF9312V
R52: 200K; EVME-SIDE; PARTNO EVM-EGGA00B25
R53, R60: 33.2K; R0805; PARTNO ERJ-6ENF3322V
R66: 10K; EVM-L4G; PARTNO EVM-L4GA00B14
R82, R83: 1.00K; R0805; PARTNO ERJ-6ENF1001V
TP3, TP4, TP5, TP6, TP7: TPTP10SQ; TP10SQ
TP8, TP10: TPS-SMD-10SN; SMD-10SN
U5: LM324D; SO14; PARTNO LM324D
U6: MT8870DS; SO18W; PARTNO MT8870DS
U7: MAX323CSA+; SO08; PARTNO MAX323CSA+
U8: MX828DW; SSOP24; PARTNO MX828DW
U9: ISD4002-240SY; SO28W; PARTNO ISD4002-240SY
U10: TLC084CD; SO14; PARTNO TLC084CD
Y2: 3.579 MHZ; TC310H; PARTNO ECS-35-18-10X
Y3: 4.032MHZ; SM49; PARTNO ECS-40.3-20-5PX-TR

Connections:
+2V5: R16.2, R46.2, R62.2, U10.1 (OUT), U10.2 (-IN)
+3V3: C68.+, C69.1, C70.+, C71.1, U9.18 (VCCA), U9.27 (VCCD); also elsewhere on the board
+5V: C30.2, C72.1, C73.1, C74.+, J2.8, R50.1, R69.2, R70.2, R74.2, R79.2, U6.18 (VDD), U8.24 (VDD); also elsewhere on the board
+12V: C75.1, C76.1, C77.1, J2.9, R73.2, U5.4 (V+), U7.8 (V+), U10.4 (V+); also elsewhere on the board
AGND: C38.1, C55.-, C56.-, C57.2, C60.2, C62.2, C63.1, C65.2, C66.2, C67.-, C68.-, C69.2, C75.2, C76.2, C77.2, C78.-, D10.A, J2.7, R26.1, R27.1, R33.1, R37.2, R38.2, R39.2, R40.2, R49.1, R61.1, R63.1, R66.1, R67.2, R71.1, R75.1, R77.1, R78.1, TP10.TP, U5.11 (V-), U7.4 (V-), U9.11 (VSSA), U9.12 (VSSA), U9.23 (VSSA), U10.11 (V-); also elsewhere on the board
AUX_AUDIO: C45.2, J2.3, R49.2; also elsewhere on the board
AUX_AUDIO_OUT: TP4.TP, U7.1 (NO), U8.22 (MOD1)
BEEP_PWM: R68.1, TP7.TP; also elsewhere on the board
CS_DTMF: U6.10 (TOE); also elsewhere on the board
DISC_AUDIO: R26.3, R27.3; also elsewhere on the board
DTMF_Q1: U6.11 (Q1); also elsewhere on the board
DTMF_Q2: U6.12 (Q2); also elsewhere on the board
DTMF_Q3: U6.13 (Q3); also elsewhere on the board
DTMF_Q4: U6.14 (Q4); also elsewhere on the board
EXP_IO0: J2.15; also elsewhere on the board
EXP_IO1: J2.19; also elsewhere on the board
EXP_IO2: J2.17; also elsewhere on the board
GND: C53.2, C54.2, C70.-, C71.2, C72.2, C73.2, C74.-, J2.6, U6.5 (INH), U6.6 (PD), U6.9 (VSS), U8.12 (VSS), U9.4 (VSSD), U9.26 (XCLK); also elsewhere on the board
I2C_SCL: J2.13; also elsewhere on the board
I2C_SDA: J2.11; also elsewhere on the board
INT_DTMF: U6.15 (STD); also elsewhere on the board
INT_EXP: J2.18, R79.1; also elsewhere on the board
INT_ISD: R69.1, U9.25 (!INT!); also elsewhere on the board
INT_MX828: R50.2, U8.7 (!IRQ!); also elsewhere on the board
INT_RAC: R70.1, U9.24 (RAC); also elsewhere on the board
MIX_BUSS: C51.1, R51.2, R59.2, R64.2, R72.1, R76.2
MIX_INSERT: C47.1, J2.4, R16.1
MUTE_AUX: U7.7 (IN); also elsewhere on the board
MUTE_RX: U7.3 (IN); also elsewhere on the board
unnamed: C45.1, R82.2
unnamed: C39.2, R26.2
unnamed: C58.1, R62.1, U7.6 (COM)
unnamed: R63.2, R64.1
unnamed: R65.2, R66.2
unnamed: C63.2, U9.16 (ANA_IN-)
unnamed: C56.+, U8.11 (A/D_CAP2)
unnamed: C52.1, R83.2
unnamed: JP4.1, R42.2
unnamed: C59.1, C60.1, R65.1, R67.1, TP8.TP
unnamed: U6.7 (OSC1), Y2.2
unnamed: U6.8 (OSC2), Y2.1
unnamed: U6.1 (IN+), U6.4 (VREF)
unnamed: C61.1, R68.2
unnamed: R75.2, R76.1
unnamed: C65.1, R73.1, R77.2, U10.12 (+IN)
unnamed: C64.2, R75.3
unnamed: C40.2, R41.2, R45.2, U6.2 (IN-)
unnamed: C41.2, JP4.3
unnamed: C40.1, R41.1, U6.3 (GS)
unnamed: C30.1, R32.2, U6.17 (ST/GT)
unnamed: R32.1, U6.16 (EST)
unnamed: C59.2, U9.17 (ANA_IN+)
unnamed: C44.2, R48.1
unnamed: C64.1, U9.13 (AUD_OUT)
unnamed: C43.2, R45.1
unnamed: C55.+, U8.10 (A/D_CAP1)
unnamed: C48.2, R56.1
unnamed: R30.2, R36.2, U5.6 (-IN), U5.7 (OUT)
unnamed: C31.1, R27.2
unnamed: C44.1, R46.1, U7.2 (COM)
unnamed: C61.2, C62.1, R71.3
unnamed: R71.2, R72.2
unnamed: C53.1, R55.2, U8.2 (XTAL/CLOCK), Y3.1
unnamed: C54.1, R55.1, U8.1 (XTAL), Y3.2
unnamed: C49.2, R54.2, U8.19 (SUM_OUT)
unnamed: R53.2, R56.2, R83.1, U10.7 (OUT)
unnamed: C39.1, R43.2
unnamed: C46.2, JP4.2, R43.1, R47.2, U8.14 (RX_AMP_IN)
unnamed: C57.1, U8.13 (VBIAS)
unnamed: C41.1, C46.1, R42.1, R47.1, U8.15 (RX_AMP_OUT)
unnamed: C48.1, R52.1, R60.2, U10.6 (-IN)
unnamed: C58.2, R63.3, R66.3
unnamed: C50.2, R59.1
unnamed: C32.2, C33.1, R33.2
unnamed: R29.2, R34.1, U5.8 (OUT)
unnamed: C36.2, R34.2, R39.1, U5.9 (-IN)
unnamed: R57.1, U8.17 (TX_AUD_OUT)
unnamed: C35.1, R30.1
unnamed: R58.1, U8.21 (TX_SUB_AUD_OUT)
unnamed: C34.2, R24.2, U5.5 (+IN)
unnamed: R52.2, R52.3, R53.1
unnamed: C67.+, U9.14 (AM_CAP)
unnamed: C42.1, R44.1, R48.2, U10.9 (-IN)
unnamed: C42.2, R44.2, R82.1, U10.8 (OUT)
unnamed: C33.2, C34.1, R36.1
unnamed: C49.1, R54.1, R57.2, R58.2, U8.18 (SUM_IN)
unnamed: C47.2, R51.1
unnamed: C29.2, C32.1, R25.2, U5.1 (OUT)
unnamed: C35.2, C36.1, R38.1, U5.10 (+IN)
unnamed: C37.1, C38.2, R29.1, U5.12 (+IN)
unnamed: C29.1, R25.1, R28.2, U5.2 (-IN)
unnamed: C31.2, R28.1
unnamed: C37.2, R35.2, R40.1, U5.13 (-IN)
unnamed: C51.2, R60.1
unnamed: C66.1, R74.1, R78.2, U10.3 (+IN)
unnamed: R31.2, R35.1, U5.14 (OUT)
RX_AUDIO_OUT: C43.1, J2.1, TP6.TP, U8.16 (RX_AUD_OUT), U8.20 (MOD1_IN)
RX_AUDIO_RET: J2.2, U7.5 (NO)
SPI_MISO: J2.14, U8.5 (REPLY_DATA), U9.3 (MISO); also elsewhere on the board
SPI_MOSI: J2.12, U8.4 (COMMAND_DATA), U9.2 (MOSI); also elsewhere on the board
SPI_SCK: J2.10, U8.3 (SERIAL_CLOCK), U9.28 (SCLK); also elsewhere on the board
SPI_SS: J2.16; also elsewhere on the board
SS_ISD: U9.1 (!SS!); also elsewhere on the board
SS_MX828: U8.6 (!CS!); also elsewhere on the board
TX_AUDIO: C52.2, J2.5, R61.2; also elsewhere on the board
TX_TONE_OUT: C50.1, TP5.TP, U8.23 (MOD2)
VREF: R24.1, U5.3 (+IN), U10.5 (+IN), U10.10 (+IN), U10.13 (-IN), U10.14 (OUT)
VSQL: C78.+, D10.C, R31.1, R37.1, TP3.TP, U8.9 (COMP_IN); also elsewhere on the board
XADC: J2.20; also elsewhere on the board

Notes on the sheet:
DTMF DECODE
CTCSS ENCODE/DECODE
REC-LEVEL
BEEP-LEVEL
INPUT
RX-LEVEL
FLAT
EMPH
PLAY-LEVEL
AUDIO EQ
CAL
VOICE REC/PLAY
OUTPUT LEVEL
MICRO-RC REPEATER CONTROLLER
EXPANSION I/O
ADJUST FOR FULL SCALE ADC READING WITH FULL NOISE PRESENT.
SET JUMPER FOR FLAT OR DE-EMPHASIZED RECEIVE AUDIO.
LEVEL
SQUELCH
REFERENCE VOLTAGES
AUDIO MIXER
PINS 1 & 2 MUST BE JUMPERED WITH NO OPTION BOARD INSTALLED.
HIGH-PASS FILTER
HF-LIMIT
NOISE RECTIFIER
200-300 mV
AUX/LINK AUDIO OUT
DC-AMP
NO RX/TX PL TONES OR RECORDER AUDIO PRESENT.
AUX/LINK AUDIO IS FILTERED RX AUDIO ONLY.
OUTPUT LEVEL IS PROGRAMMED BY MX828 ATTENUATOR

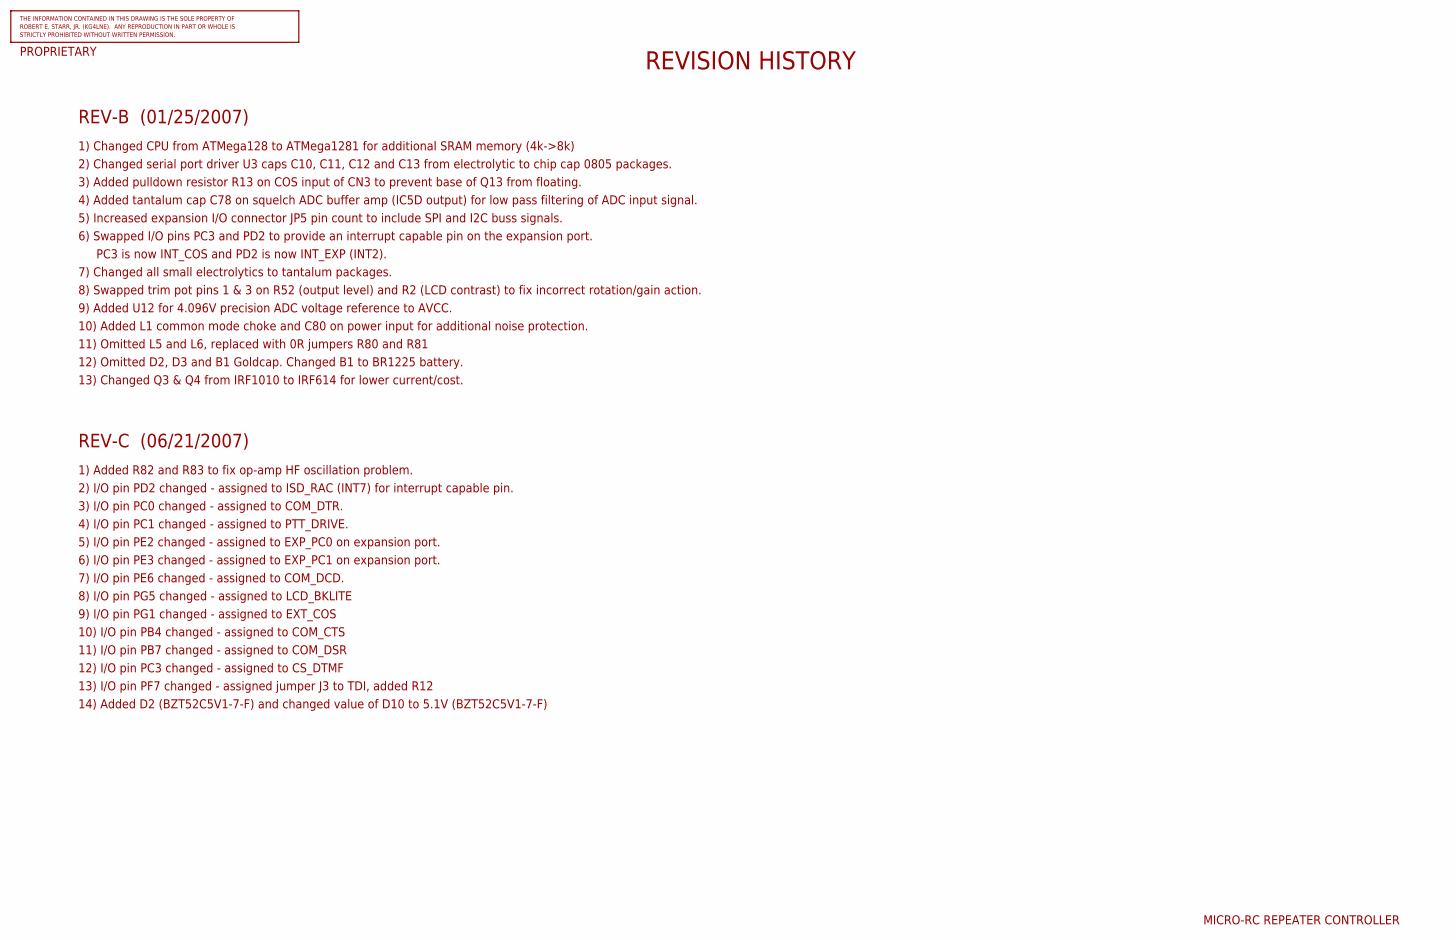
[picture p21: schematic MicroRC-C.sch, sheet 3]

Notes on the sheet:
MICRO-RC REPEATER CONTROLLER
REVISION HISTORY
REV-B (01/25/2007)
2) Changed serial port driver U3 caps C10, C11, C12 and C13 from electrolytic to chip cap 0805 packages.
4) Added tantalum cap C78 on squelch ADC buffer amp (IC5D output) for low pass filtering of ADC input signal.
5) Increased expansion I/O connector JP5 pin count to include SPI and I2C buss signals.
3) Added pulldown resistor R13 on COS input of CN3 to prevent base of Q13 from floating.
6) Swapped I/O pins PC3 and PD2 to provide an interrupt capable pin on the expansion port.
PC3 is now INT_COS and PD2 is now INT_EXP (INT2).
7) Changed all small electrolytics to tantalum packages.
8) Swapped trim pot pins 1 & 3 on R52 (output level) and R2 (LCD contrast) to fix incorrect rotation/gain action.
9) Added U12 for 4.096V precision ADC voltage reference to AVCC.
1) Changed CPU from ATMega128 to ATMega1281 for additional SRAM memory (4k->8k)
10) Added L1 common mode choke and C80 on power input for additional noise protection.
11) Omitted L5 and L6, replaced with 0R jumpers R80 and R81
12) Omitted D2, D3 and B1 Goldcap. Changed B1 to BR1225 battery.
13) Changed Q3 & Q4 from IRF1010 to IRF614 for lower current/cost.
REV-C (06/21/2007)
1) Added R82 and R83 to fix op-amp HF oscillation problem.
2) I/O pin PD2 changed - assigned to ISD_RAC (INT7) for interrupt capable pin.
5) I/O pin PE2 changed - assigned to EXP_PC0 on expansion port.
14) Added D2 (BZT52C5V1-7-F) and changed value of D10 to 5.1V (BZT52C5V1-7-F)
4) I/O pin PC1 changed - assigned to PTT_DRIVE.
6) I/O pin PE3 changed - assigned to EXP_PC1 on expansion port.
7) I/O pin PE6 changed - assigned to COM_DCD.
3) I/O pin PC0 changed - assigned to COM_DTR.
8) I/O pin PG5 changed - assigned to LCD_BKLITE
9) I/O pin PG1 changed - assigned to EXT_COS
10) I/O pin PB4 changed - assigned to COM_CTS
11) I/O pin PB7 changed - assigned to COM_DSR
13) I/O pin PF7 changed - assigned jumper J3 to TDI, added R12
12) I/O pin PC3 changed - assigned to CS_DTMF

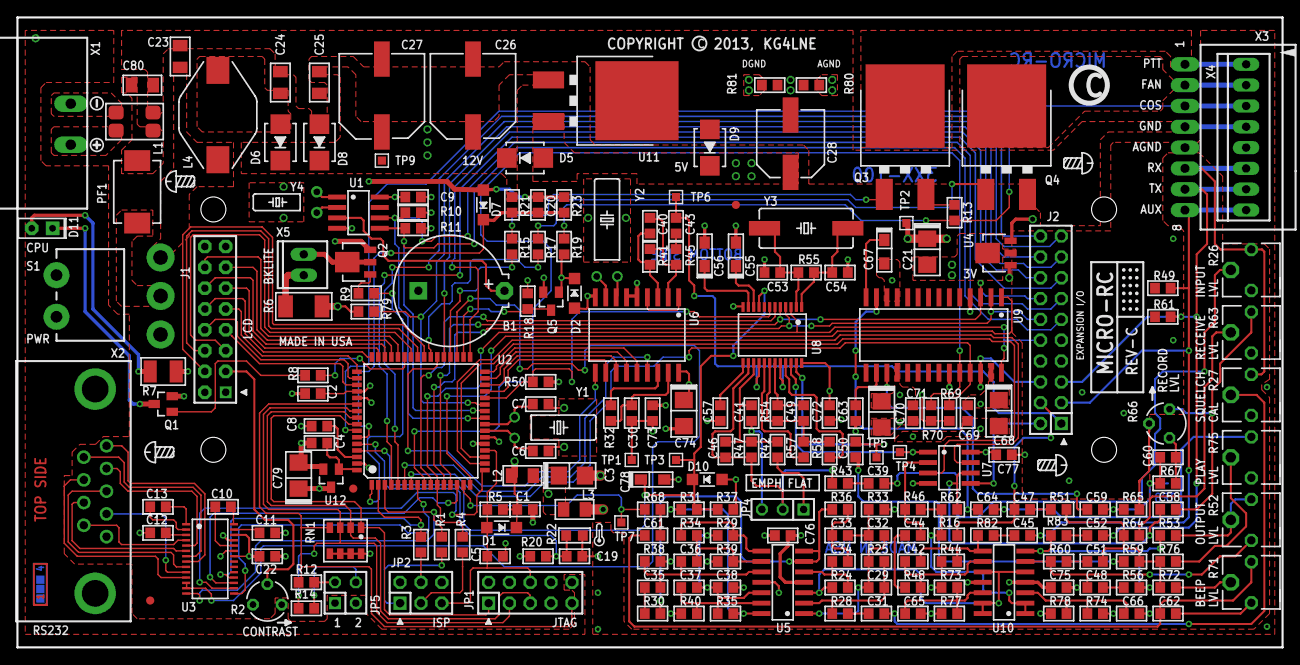
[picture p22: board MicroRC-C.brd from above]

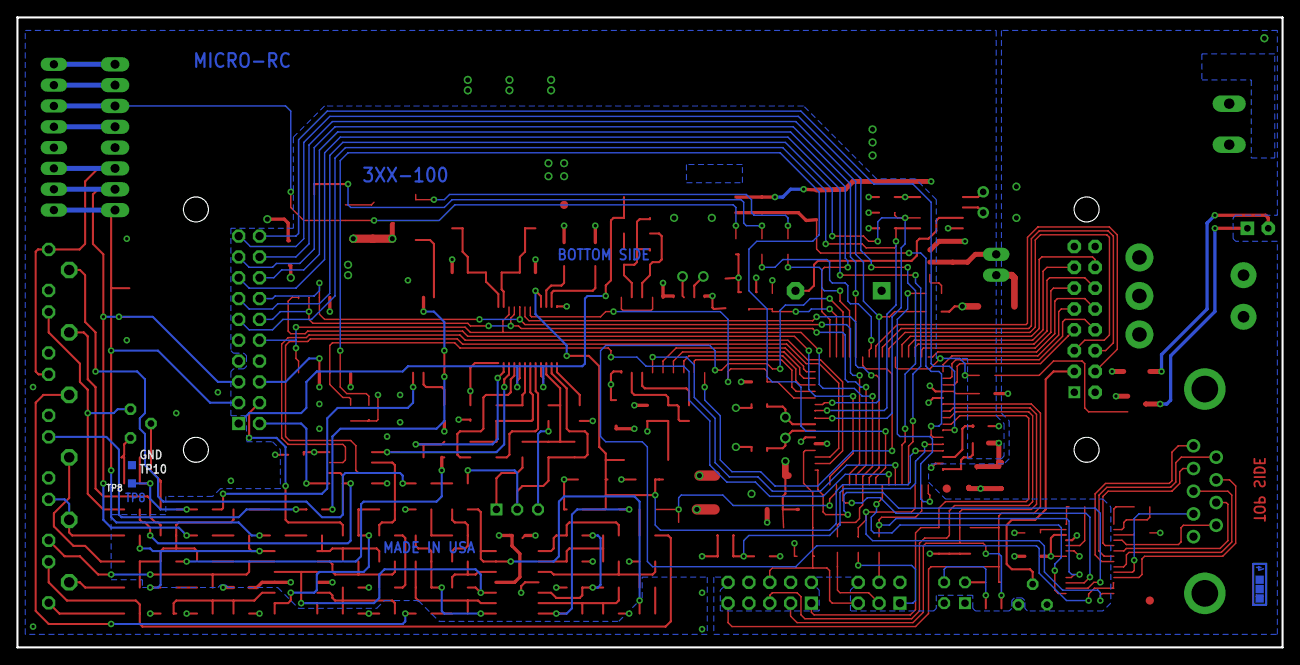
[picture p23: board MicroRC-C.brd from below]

Board: 4 copper layers, 154.3 x 76.8 mm, 254 parts (3 on the bottom side), 186 nets.

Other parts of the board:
U$6: ICON_ATTR_COPYRIGHT
U$7: LAYER_CHECK-4
U$60: FIELD_ATTR_DATECODE5_RESTRICT
U$74: ICON_SIDE_BOTTOM
U$75: ICON_SIDE_TOP
U$100: ICON_ATTR_REV-M
U$102: FAB_8X14
U$105: FAB_DOCFIELD
U$112: ICON_TEMP
U$123: ICON_MINUS
U$124: 3.0250; FAB_ARROW_LINE025
U$125: ICON_PLUS
U$128, U$136: 0,0; FAB_ARROW_LINE025
U$132: 2.7125; FAB_CONST_LINE050
U$133, U$239, U$282, U$283: ICON_MSCREW-S
U$138: 6.0750; FAB_ARROW_LINE025
U$139: 0.5750; FAB_CONST_LINE050
U$140: 1.2125; FAB_CONST_LINE050
U$141: 1.5125; FAB_CONST_LINE050
U$142: 1.8125; FAB_CONST_LINE050
U$143: 2.1125; FAB_CONST_LINE050
U$144: 2.4125; FAB_CONST_LINE050
U$145: 1.3375; FAB_CONST_LINE050
U$146: 2.2750; FAB_CONST_LINE050
U$230, U$235, U$280, U$281: ICON_PIN1_B
U$240, U$241: ICON_ARROW-T

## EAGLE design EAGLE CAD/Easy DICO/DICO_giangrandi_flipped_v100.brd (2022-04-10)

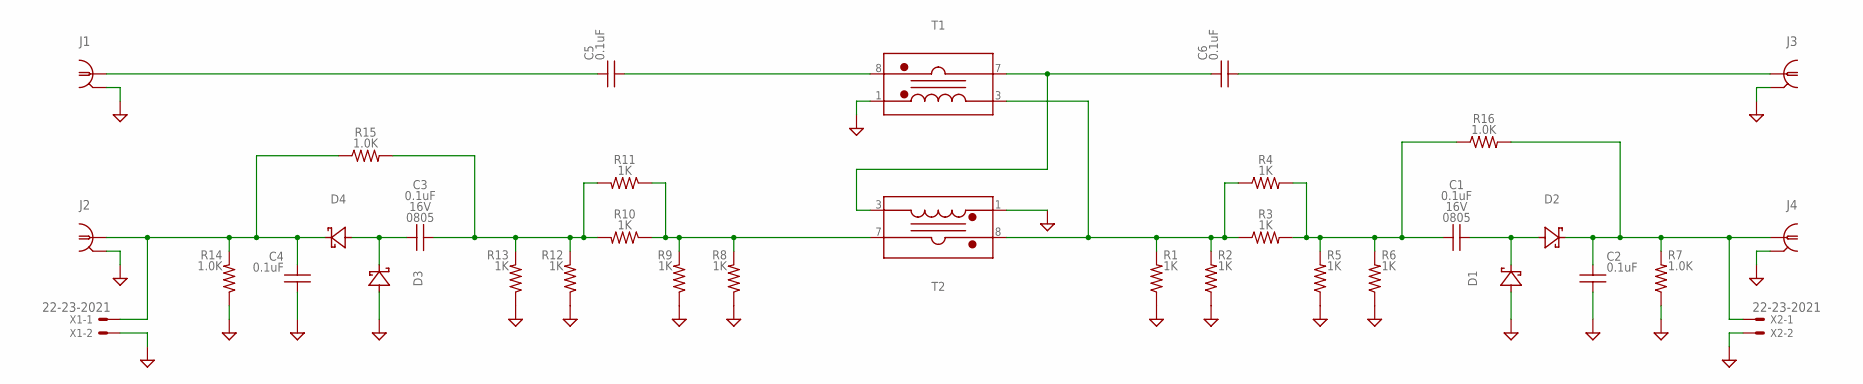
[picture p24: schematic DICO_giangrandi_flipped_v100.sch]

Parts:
C1, C2, C3, C4: 0.1uF; 0805_IPC-7351B
C5, C6: 0.1uF; C1812
D1, D2, D3, D4: D-SCHOTTKY1N5711W-7-FSOD123; SOD123
J1, J2, J3, J4: COAXSMA_0.375WIDE; SMA_EDGE_0.375WIDE
R1, R2, R3, R4, R5, R6, R8, R9, R10, R11, R12, R13: 1K; 1206_IPC-7351B
R7, R14, R15, R16: 1.0K; 0805_IPC-7351B
T1, T2: TRAFO_CURRENTSENSEPA1005_NOCENTERPADS; PA1005_NOCENTERPADS
X1, X2: 22-23-2021

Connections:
GND: C2.2, C4.2, D1.A (A1), D3.A (A1), J1.S1 (GND1), J1.S2 (GND1), J1.S3 (GND1), J1.S4 (GND1), J2.S1 (GND1), J2.S2 (GND1), J2.S3 (GND1), J2.S4 (GND1), J3.S1 (GND1), J3.S2 (GND1), J3.S3 (GND1), J3.S4 (GND1), J4.S1 (GND1), J4.S2 (GND1), J4.S3 (GND1), J4.S4 (GND1), R1.2, R2.2, R5.2, R6.2, R7.2, R8.2, R9.2, R12.2, R13.2, R14.2, T1.1 (SS), T2.1 (SS), X1.2, X2.2
unnamed: R8.1, R9.1, R10.1, R11.1, T2.7 (PF)
unnamed: C5.2, T1.8 (PS)
unnamed: C5.1, J1.C (1)
unnamed: C1.1, R3.2, R4.2, R5.1, R6.1, R16.1
unnamed: C1.2, D1.K (C1), D2.A (A1)
unnamed: C2.1, D2.K (C1), J4.C (1), R7.1, R16.2, X2.1
unnamed: C3.1, R10.2, R11.2, R12.1, R13.1, R15.2
unnamed: C3.2, D3.K (C1), D4.A (A1)
unnamed: C4.1, D4.K (C1), J2.C (1), R14.1, R15.1, X1.1
unnamed: C6.2, J3.C (1)
unnamed: R1.1, R2.1, R3.1, R4.1, T1.3 (SF), T2.8 (PS)
unnamed: C6.1, T1.7 (PF), T2.3 (SF)

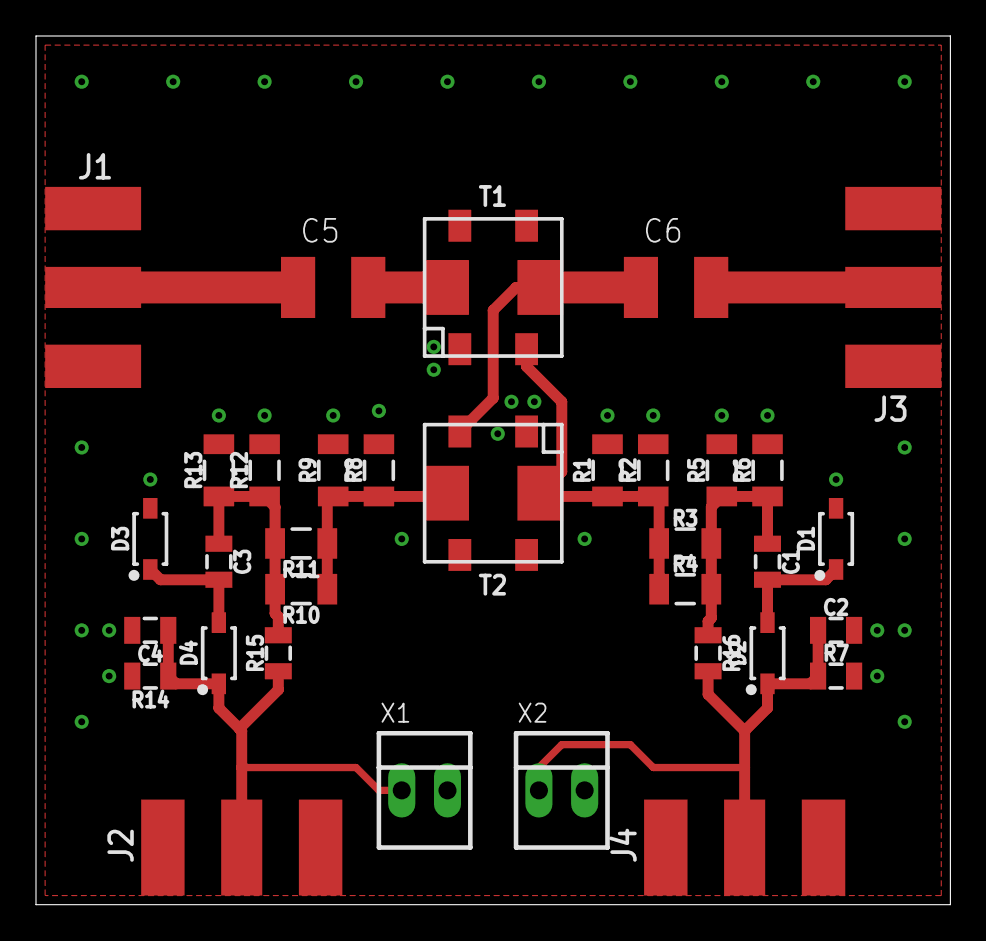
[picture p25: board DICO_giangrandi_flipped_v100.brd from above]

Board: 2 copper layers, 50.8 x 48.3 mm, 34 parts (0 on the bottom side), 13 nets.

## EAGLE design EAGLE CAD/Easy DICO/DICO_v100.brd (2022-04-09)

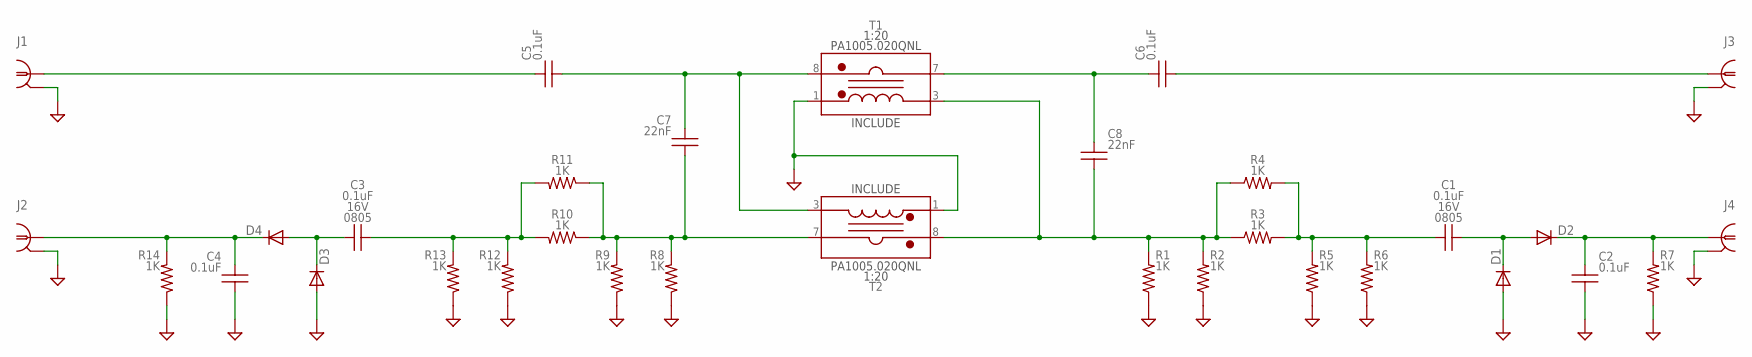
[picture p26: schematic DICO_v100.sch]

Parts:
C1, C2, C3, C4: 0.1uF; 0805_IPC-7351B
C5, C6: 0.1uF; C1812
C7, C8: 22nF; C1206
D1, D2, D3, D4: DIODE-SOD123; SOD123
J1, J2, J3, J4: COAXBNC_EDGE; BNC_EDGE
R1, R2, R3, R4, R5, R6, R7, R8, R9, R10, R11, R12, R13, R14: 1K; R1206
T1, T2: TRAFO_CURRENTSENSEPA1005.020QNLPA1005; PA1005

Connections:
GND: C2.2, C4.2, D1.A, D3.A, J1.G1 (GND1), J1.G2 (GND1), J1.G3 (GND1), J1.G4 (GND1), J2.G1 (GND1), J2.G2 (GND1), J2.G3 (GND1), J2.G4 (GND1), J3.G1 (GND1), J3.G2 (GND1), J3.G3 (GND1), J3.G4 (GND1), J4.G1 (GND1), J4.G2 (GND1), J4.G3 (GND1), J4.G4 (GND1), R1.2, R2.2, R5.2, R6.2, R7.2, R8.2, R9.2, R12.2, R13.2, R14.2, T1.1 (SS), T2.1 (SS)
unnamed: C8.2, R1.1, R2.1, R3.1, R4.1, T1.3 (SF), T2.8 (PS)
unnamed: C5.2, C7.1, T1.8 (PS), T2.3 (SF)
unnamed: C6.1, C8.1, T1.7 (PF)
unnamed: C5.1, J1.C (1)
unnamed: C1.1, R3.2, R4.2, R5.1, R6.1
unnamed: C1.2, D1.C, D2.A
unnamed: C2.1, D2.C, J4.C (1), R7.1
unnamed: C7.2, R8.1, R9.1, R10.1, R11.1, T2.7 (PF)
unnamed: C3.1, R10.2, R11.2, R12.1, R13.1
unnamed: C3.2, D3.C, D4.A
unnamed: C4.1, D4.C, J2.C (1), R14.1
unnamed: C6.2, J3.C (1)

Board: 2 copper layers, 32 parts (0 on the bottom side), 13 nets, no tracks yet.

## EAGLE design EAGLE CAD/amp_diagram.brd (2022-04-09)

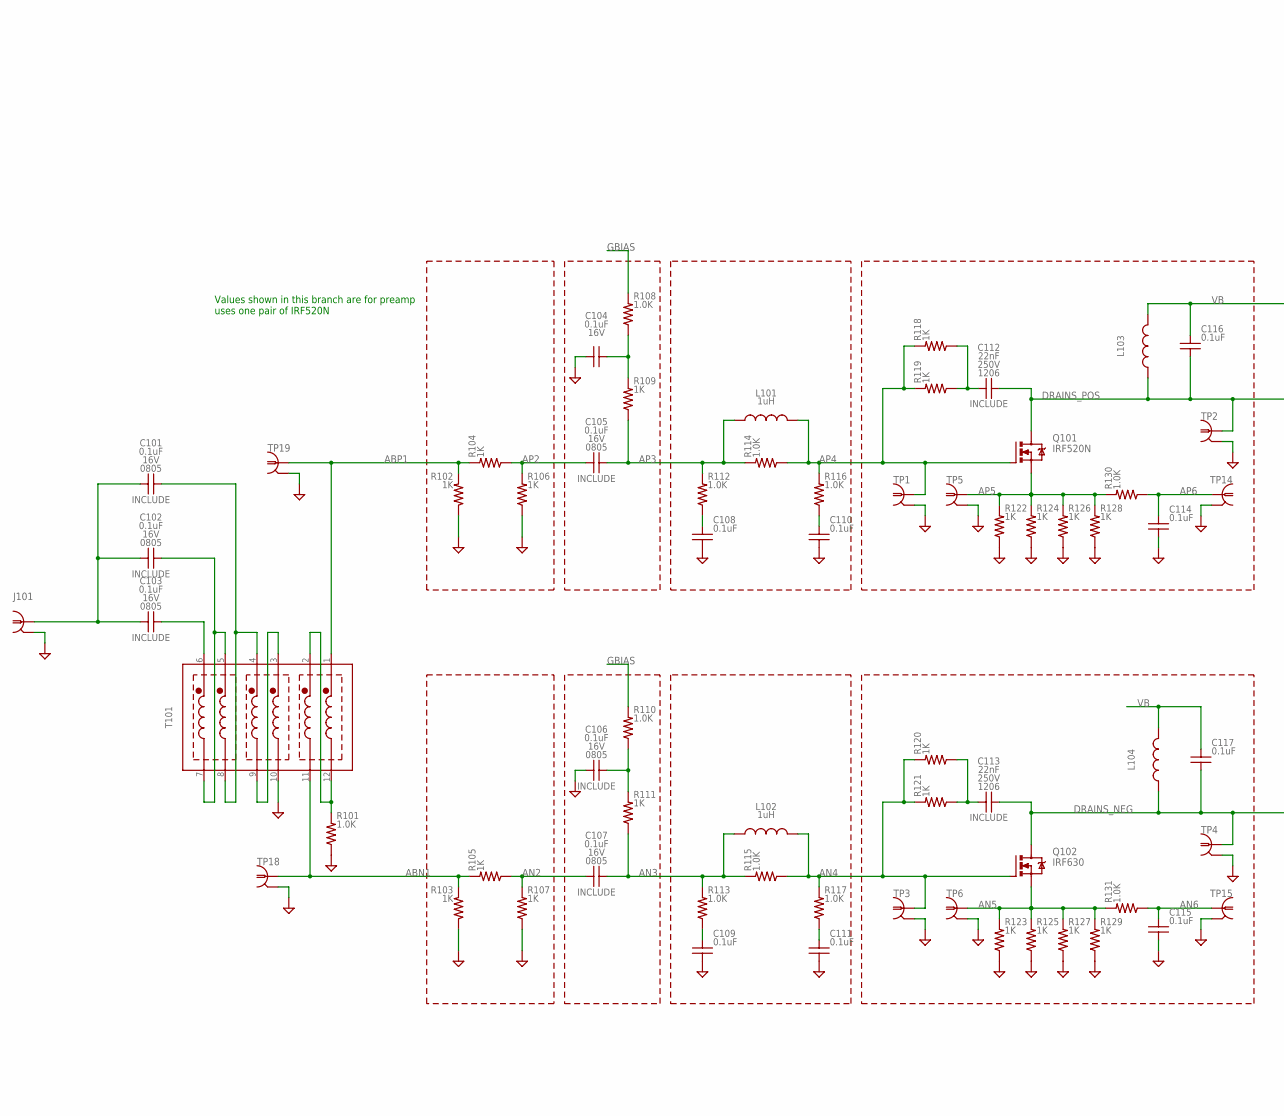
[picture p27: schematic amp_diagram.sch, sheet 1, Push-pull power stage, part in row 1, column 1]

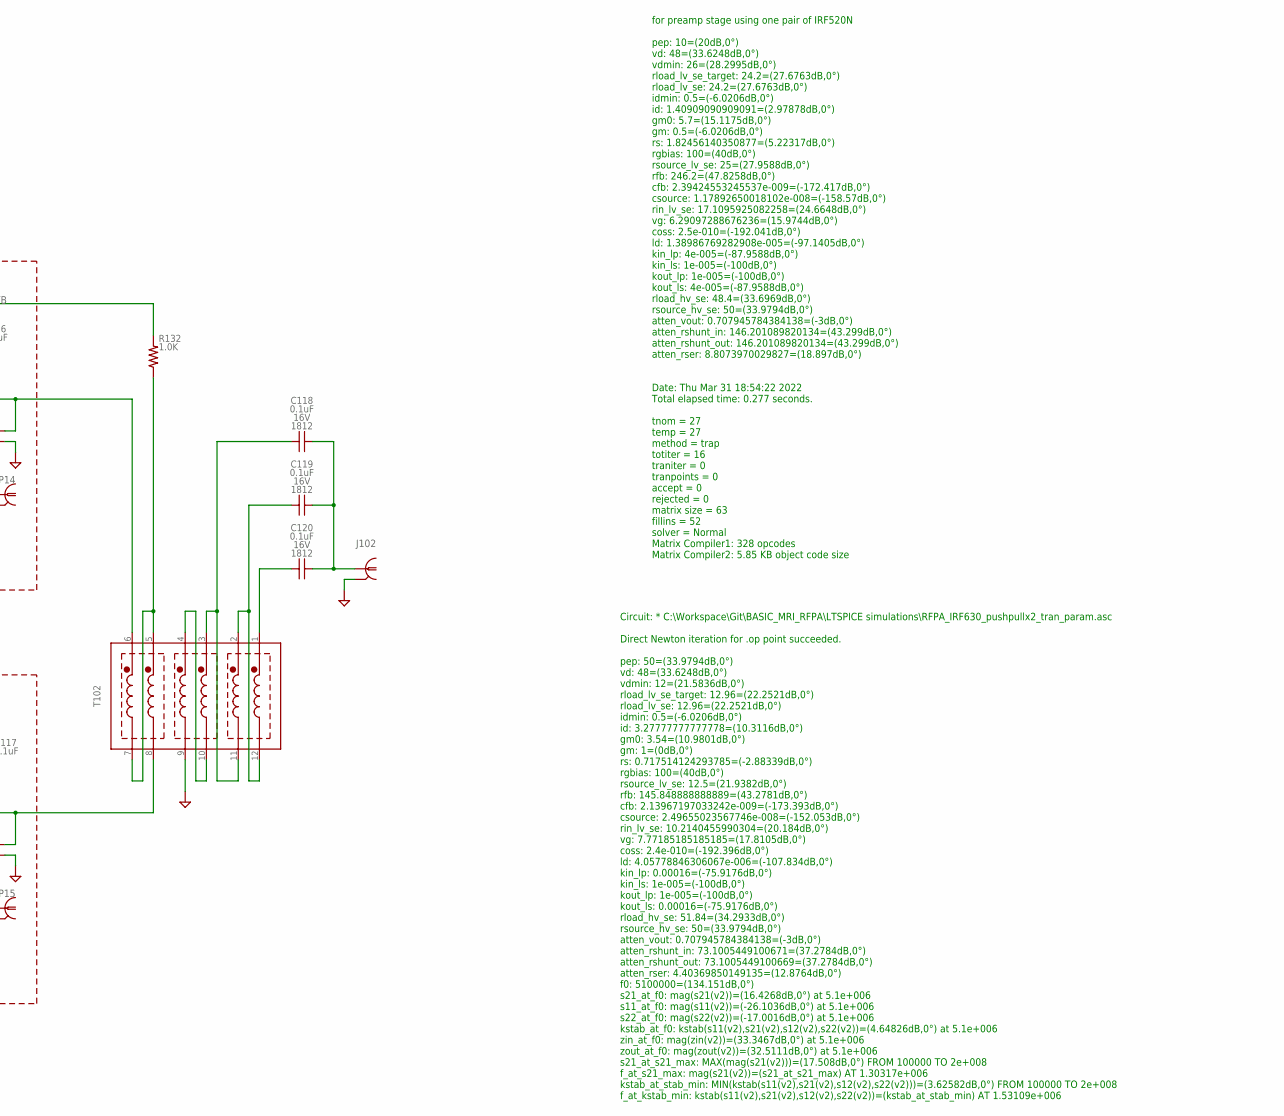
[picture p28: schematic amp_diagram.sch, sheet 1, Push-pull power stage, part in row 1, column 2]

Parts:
C101, C102, C103, C104, C105, C106, C107, C108, C109, C110, C111, C114, C115: 0.1uF; 0805_IPC-7351B
C112, C113: 22nF; C1206
C116, C117, C118, C119, C120: 0.1uF; C1812
J101, J102: COAXBNC_EDGE; BNC_EDGE
L101, L102: 1uH; L1008
L103, L104: L; DR127
Q101: IRF520N; TO220BV
Q102: IRF630; TO220BV
R101, R108, R110, R112, R113, R114, R115, R116, R117, R130, R131, R132: 1.0K; 0805_IPC-7351B
R102, R103, R104, R105, R106, R107, R109, R111: 1K; R1206
R118, R119, R120, R121, R122, R123, R124, R125, R126, R127, R128, R129: 1K; R2512
T101, T102: HP4_TRAFO; HP4
TP1, TP3, TP14, TP15, TP18, TP19: PROBE_TPTP_5MM; PROBE_TP_5MM
TP2, TP4, TP5, TP6: PROBE_TPTP_7P5MM; PROBE_TP_7P5MM

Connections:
ABN1: R103.1, R105.1, T101.11 (F2), TP18.TP (1); also elsewhere on the board
ABP1: R102.1, R104.1, T101.1 (S1), TP19.TP (1); also elsewhere on the board
AN2: C107.2, R105.2, R107.1
AN3: C107.1, L102.1, R111.2, R113.1, R115.1
AN4: L102.2, Q102.G, R115.2, R117.1, R120.1, R121.1, TP3.TP (1)
AN5: Q102.S, R123.1, R125.1, R127.1, R129.1, R131.1, TP6.TP (1)
AN6: C115.1, R131.2, TP15.TP (1)
AP2: C105.2, R104.2, R106.1
AP3: C105.1, L101.1, R109.2, R112.1, R114.1
AP4: L101.2, Q101.G, R114.2, R116.1, R118.1, R119.1, TP1.TP (1)
AP5: Q101.S, R122.1, R124.1, R126.1, R128.1, R130.1, TP5.TP (1); also elsewhere on the board
AP6: C114.1, R130.2, TP14.TP (1)
DRAINS_NEG: C113.2, C117.2, L104.1, Q102.D, T102.8 (F5), TP4.TP (1); also elsewhere on the board
DRAINS_POS: C112.2, C116.2, L103.1, Q101.D, T102.6 (S6), TP2.TP (1); also elsewhere on the board
GBIAS: R108.1, R110.1; also elsewhere on the board
GND: C104.2, C106.2, C108.2, C109.2, C110.2, C111.2, C114.2, C115.2, J101.G1 (GND1), J101.G2 (GND1), J101.G3 (GND1), J101.G4 (GND1), J102.G1 (GND1), J102.G2 (GND1), J102.G3 (GND1), J102.G4 (GND1), R101.2, R102.2, R103.2, R106.2, R107.2, R122.2, R123.2, R124.2, R125.2, R126.2, R127.2, R128.2, R129.2, T101.10 (F3), T102.9 (F4), TP1.GND (GND1), TP2.GND (GND1), TP3.GND (GND1), TP4.GND (GND1), TP5.GND (GND1), TP6.GND (GND1), TP14.GND (GND1), TP15.GND (GND1), TP18.GND (GND1), TP19.GND (GND1); also elsewhere on the board
unnamed: C113.1, R120.2, R121.2
unnamed: C109.1, R113.2
unnamed: C104.1, R108.2, R109.1
unnamed: C108.1, R112.2
unnamed: C110.1, R116.2
unnamed: C112.1, R118.2, R119.2
unnamed: C106.1, R110.2, R111.1
unnamed: C111.1, R117.2
unnamed: T101.3 (S3), T101.9 (F4)
unnamed: R101.1, T101.2 (S2), T101.12 (F1)
unnamed: C119.1, T102.2 (S2), T102.12 (F1)
unnamed: C120.1, T102.1 (S1)
unnamed: C118.2, C119.2, C120.2, J102.C (1)
unnamed: C101.2, C102.2, C103.2, J101.C (1)
unnamed: C103.1, T101.6 (S6)
unnamed: C118.1, T102.3 (S3), T102.11 (F2)
unnamed: C101.1, T101.4 (S4), T101.8 (F5)
unnamed: T102.4 (S4), T102.10 (F3)
VB: C116.1, C117.1, L103.2, L104.2, R132.1; also elsewhere on the board
VB_CT: R132.2, T102.5 (S5), T102.7 (F6)
VB_CT1: C102.1, T101.5 (S5), T101.7 (F6)

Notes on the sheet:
for preamp stage using one pair of IRF520N pep: 10=(20dB,0°) vd: 48=(33.6248dB,0°) vdmin: 26=(28.2995dB,0°) rload_lv_se_target: 24.2=(27.6763dB,0°) rload_lv_se: 24.2=(27.6763dB,0°) idmin: 0.5=(-6.0206dB,0°) id: 1.40909090909091=(2.97878dB,0°) gm0: 5.7=(15.1175dB,0°) gm: 0.5=(-6.0206dB,0°) rs: 1.824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
Values shown in this branch are for preamp uses one pair of IRF520N
Circuit: * C:\Workspace\Git\BASIC_MRI_RFPA\LTSPICE simulations\RFPA_IRF630_pushpullx2_tran_param.asc Direct Newton iteration for .op point succeeded. pep: 50=(33.9794dB,0°) vd: 48=(33.6248dB,0°) vdmin: 12=(21.5836dB,0°) rload_lv_se_target: 12.96=(22.2521dB,0°) rload_lv_se: 12.96=(22.2521dB,0°) idmi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

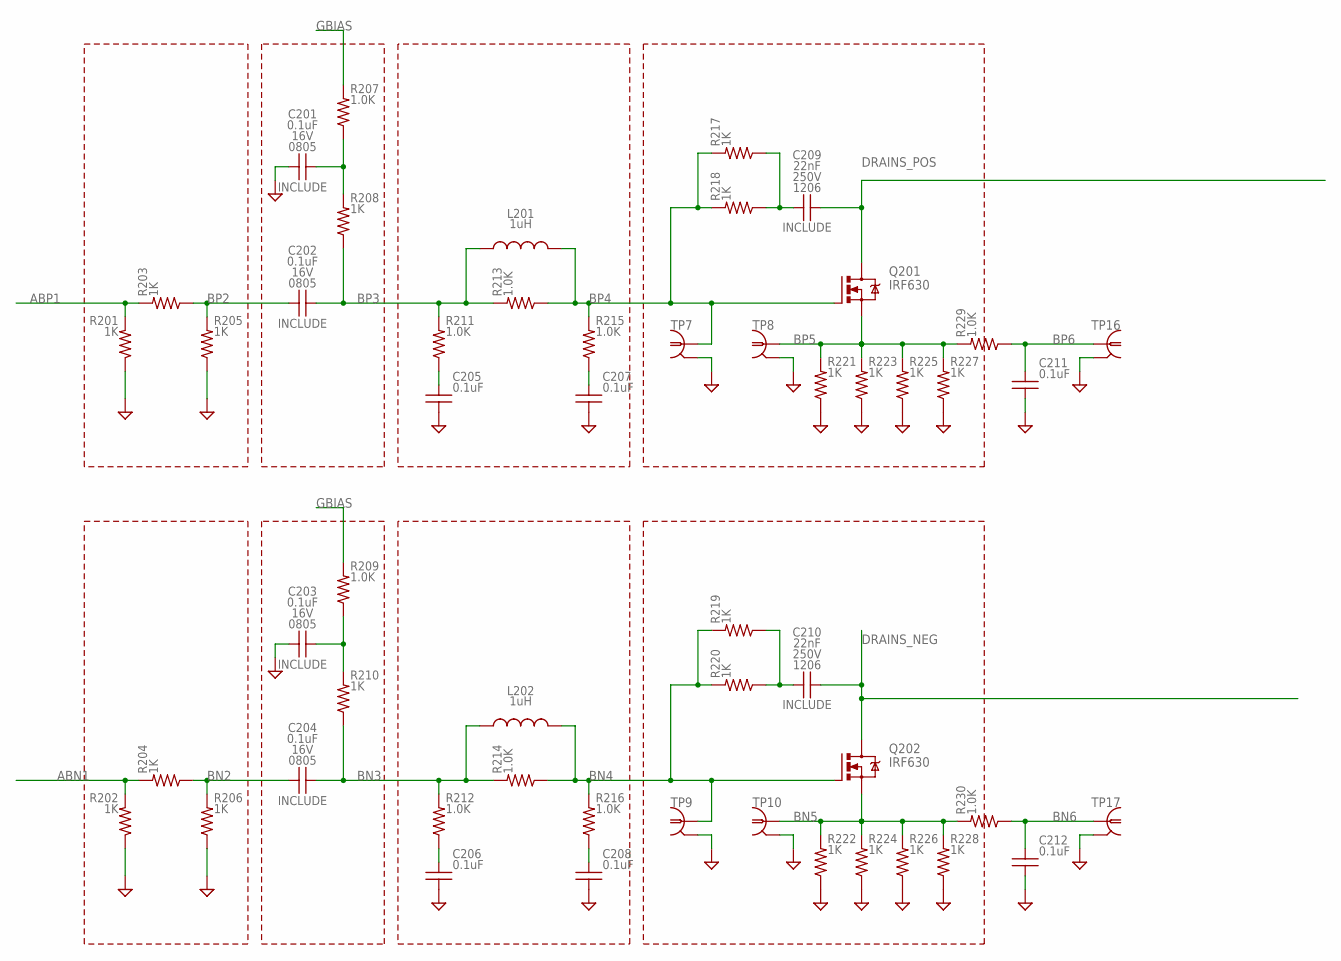
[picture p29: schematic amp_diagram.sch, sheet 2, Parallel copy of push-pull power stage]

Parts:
C201, C202, C203, C204, C205, C206, C207, C208, C211, C212: 0.1uF; 0805_IPC-7351B
C209, C210: 22nF; C1206
L201, L202: 1uH; L1008
Q201, Q202: IRF630; TO220BV
R201, R202, R203, R204, R205, R206, R208, R210: 1K; R1206
R207, R209, R211, R212, R213, R214, R215, R216, R229, R230: 1.0K; 0805_IPC-7351B
R217, R218, R219, R220, R221, R222, R223, R224, R225, R226, R227, R228: 1K; R2512
TP7, TP9, TP10, TP16: PROBE_TPTP_5MM; PROBE_TP_5MM
TP8, TP17: PROBE_TPTP_7P5MM; PROBE_TP_7P5MM

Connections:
ABN1: R202.1, R204.1; also elsewhere on the board
ABP1: R201.1, R203.1; also elsewhere on the board
BN2: C204.2, R204.2, R206.1
BN3: C204.1, L202.1, R210.2, R212.1, R214.1
BN4: L202.2, Q202.G, R214.2, R216.1, R219.1, R220.1, TP9.TP (1)
BN5: Q202.S, R222.1, R224.1, R226.1, R228.1, R230.1, TP10.TP (1)
BN6: C212.1, R230.2, TP17.TP (1)
BP2: C202.2, R203.2, R205.1
BP3: C202.1, L201.1, R208.2, R211.1, R213.1
BP4: L201.2, Q201.G, R213.2, R215.1, R217.1, R218.1, TP7.TP (1)
BP5: Q201.S, R221.1, R223.1, R225.1, R227.1, R229.1, TP8.TP (1)
BP6: C211.1, R229.2, TP16.TP (1)
DRAINS_NEG: C210.2, Q202.D; also elsewhere on the board
DRAINS_POS: C209.2, Q201.D; also elsewhere on the board
GBIAS: R207.1, R209.1; also elsewhere on the board
GND: C201.2, C203.2, C205.2, C206.2, C207.2, C208.2, C211.2, C212.2, R201.2, R202.2, R205.2, R206.2, R221.2, R222.2, R223.2, R224.2, R225.2, R226.2, R227.2, R228.2, TP7.GND (GND1), TP8.GND (GND1), TP9.GND (GND1), TP10.GND (GND1), TP16.GND (GND1), TP17.GND (GND1); also elsewhere on the board
unnamed: C203.1, R209.2, R210.1
unnamed: C206.1, R212.2
unnamed: C208.1, R216.2
unnamed: C210.1, R219.2, R220.2
unnamed: C201.1, R207.2, R208.1
unnamed: C205.1, R211.2
unnamed: C207.1, R215.2
unnamed: C209.1, R217.2, R218.2

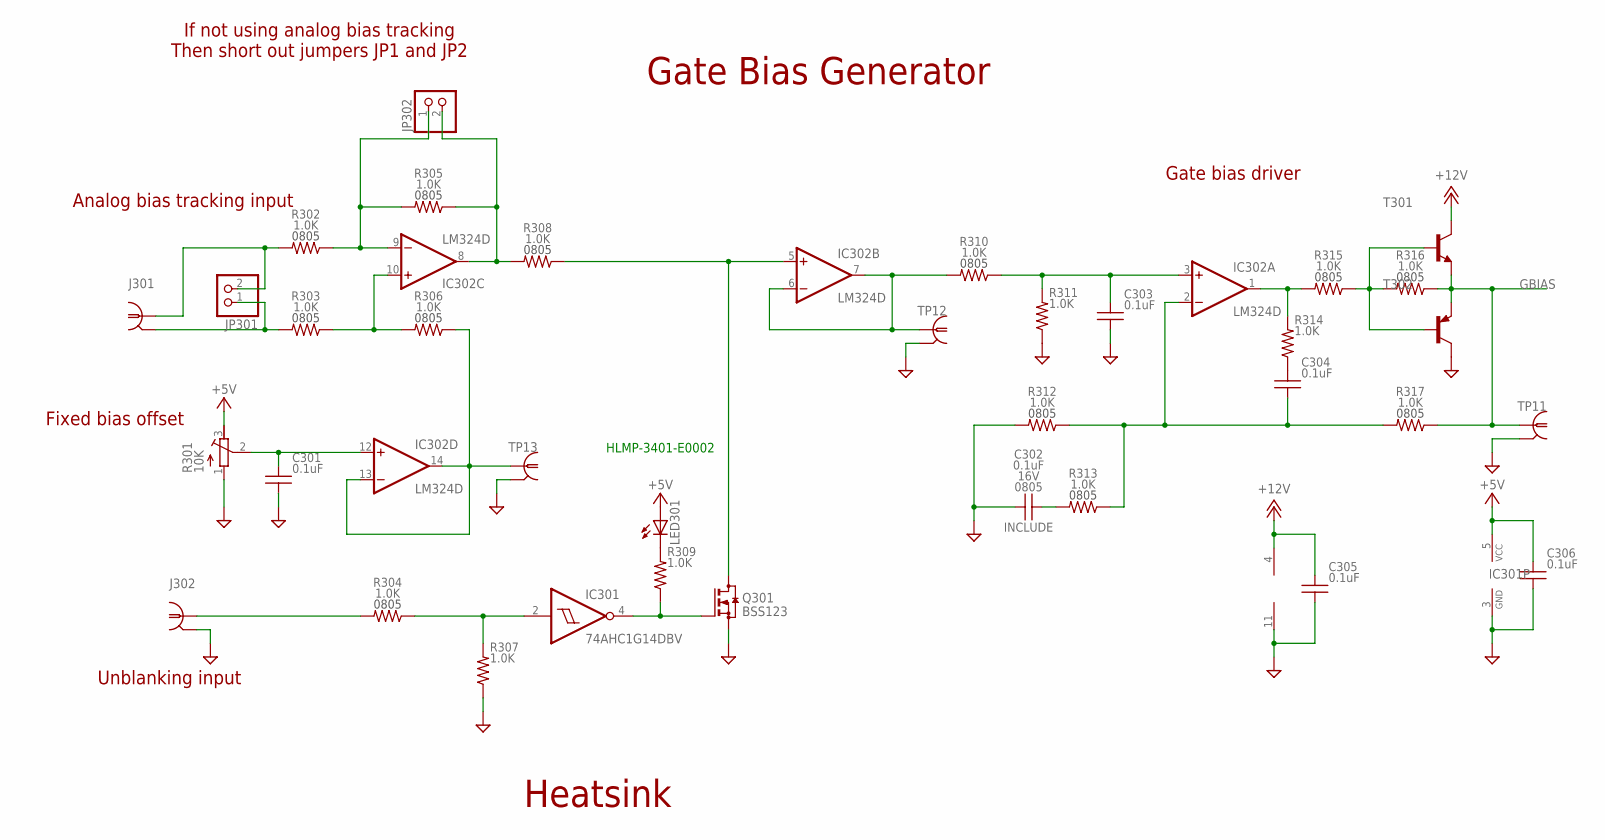
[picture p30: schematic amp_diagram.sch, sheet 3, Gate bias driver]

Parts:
C301, C302, C303, C304, C305, C306: 0.1uF; 0805_IPC-7351B
IC301: 74AHC1G14DBV; SOT23-5
IC302: LM324D; SO14
J301, J302: COAXBNC_EDGE; BNC_EDGE
JP301, JP302: PINHD-1X2; 1X02
LED301: LED5MM
Q301: BSS123; SOT23
R301: 10K; RTRIM3299W
R302, R303, R304, R305, R306, R307, R308, R309, R310, R311, R312, R313, R314, R315, R316, R317: 1.0K; 0805_IPC-7351B
T301: BC808-NPN-SOT23-BEC; SOT23-BEC
T302: BC807-16-PNP-SOT23-BEC; SOT23-BEC
TP11, TP12, TP13: PROBE_TPTP_5MM; PROBE_TP_5MM

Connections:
+5V: C306.1, IC301.5 (VCC), LED301.A, R301.3 (E); also elsewhere on the board
+12V: C305.1, IC302.4 (V+), T301.C; also elsewhere on the board
GBIAS: R316.2, R317.2, T301.E, T302.E, TP11.TP (1); also elsewhere on the board
GND: C301.2, C302.2, C303.2, C305.2, C306.2, IC301.3 (GND), IC302.11 (V-), J302.G1 (GND1), J302.G2 (GND1), J302.G3 (GND1), J302.G4 (GND1), Q301.2 (S), R301.1 (A), R307.2, R311.2, R312.1, T302.C, TP11.GND (GND1), TP12.GND (GND1), TP13.GND (GND1); also elsewhere on the board
unnamed: IC302.1 (OUT), R314.1, R315.1
unnamed: R315.2, R316.1, T301.B, T302.B
unnamed: IC301.2 (I), R304.2, R307.1
unnamed: IC302.6 (-IN), IC302.7 (OUT), R310.1, TP12.TP (1)
unnamed: C304.1, R314.2
unnamed: C302.1, R313.1
unnamed: C304.2, IC302.2 (-IN), R312.2, R313.2, R317.1
unnamed: C303.1, IC302.3 (+IN), R310.2, R311.1
unnamed: IC302.10 (+IN), R303.2, R306.1
unnamed: IC302.8 (OUT), JP302.2, R305.2, R308.1
unnamed: IC302.9 (-IN), JP302.1, R302.2, R305.1
unnamed: J301.C (1), JP301.2, R302.1
unnamed: J301.G1 (GND1), J301.G2 (GND1), J301.G3 (GND1), J301.G4 (GND1), JP301.1, R303.1
unnamed: IC302.5 (+IN), Q301.3 (D), R308.2
unnamed: IC301.4 (O), Q301.1 (G), R309.2
unnamed: C301.1, IC302.12 (+IN), R301.2 (S)
unnamed: IC302.13 (-IN), IC302.14 (OUT), R306.2, TP13.TP (1)
unnamed: LED301.K (C), R309.1
unnamed: J302.C (1), R304.1

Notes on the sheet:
Gate Bias Generator
Heatsink
If not using analog bias tracking Then short out jumpers JP1 and JP2
Analog bias tracking input
Fixed bias offset
Gate bias driver
Unblanking input
‎HLMP-3401-E0002‎


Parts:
C401: 3300uF; EB25D
C402, C405, C408, C411, C412, C413: 10uF; C2220_CKG57N
C403, C404: 6.8uF; C1210
C406, C407: 47nF; C1206
C409, C410: 22uF; E2,5-7
D401: D-SCHOTTKYSK810L-TPSMC; DO-214AB(SMC)
D402: D-ZENER1N5355B-TPDO15-12; DO15-12
H401, H402, H403, H404: MOUNT-PAD-SQUARE3.2; 3,2-PAD-SQUARE
IC401, IC402: 78XXS
J401: FUSE_2P; 02540121Z
J402: KK_PCFAN; 47053-1000
L401: 3.3uH; DR127
L402: 22uH; DR127
LED401, LED402: LED5MM
R401, R402, R403, R404: 1.0; R1206
R405: 0.5; R1206
R406: 2K; 0805_IPC-7351B
R407: 590; 0805_IPC-7351B
R408: 10K; 0805_IPC-7351B
X401: W237-102
X402: HEATSINK_OMNI_DUAL30-75-D; OMNI-UNI-30-75-D

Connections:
+5V: C407.1, C410.+, IC402.OUT, LED402.A, R408.1; also elsewhere on the board
+12V: C406.1, C409.+, IC401.OUT, J402.2, LED401.A; also elsewhere on the board
GND: C401.-, C402.2, C403.2, C404.2, C405.2, C406.2, C407.2, C408.2, C409.-, C410.-, C411.2, C412.2, C413.2, D401.A (A1), H401.B3,2, H402.B3,2, H403.B3,2, H404.B3,2, IC401.GND, IC402.GND, J402.1, R406.2, R407.2, X401.2, X402.P1, X402.P2; also elsewhere on the board
unnamed: D402.A (A1), R402.1, R403.1
unnamed: LED401.K (C), R406.1
unnamed: LED402.K (C), R407.1
unnamed: C403.1, IC401.IN, R402.2
unnamed: D401.K (C1), J401.2, R401.1
unnamed: J401.1, X401.1
unnamed: C401.+, C402.1, D402.C (C1), L401.1, R401.2
unnamed: C405.1, L401.2, L402.1, R404.1, R405.1
unnamed: C404.1, IC402.IN, R403.2
unnamed: J402.3, R408.2
VB: C408.1, C411.1, C412.1, C413.1, L402.2, R404.2, R405.2; also elsewhere on the board

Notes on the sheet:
LDOs
Heatsink
PAC300001008FAC000
DR127-220-R
DR127-3R3-R
1N5355B-TP
HLMP-3962-F0002‎
860010773010
SK810L-TP


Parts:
C1: 22nF; C1206
C3: 0.1uF; C1812
L1: L; DR127
Q1, Q2: IRF520N; TO220BV
R1, R2, R3, R4, R5: 1K; R2512
TP20: PROBE_TPTP_7P5MM; PROBE_TP_7P5MM

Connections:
AP1: Q2.G
AP5: Q2.S, R2.1; also elsewhere on the board
DRAINS_POS: C1.2, C3.2, L1.1, Q2.D, TP20.TP (1); also elsewhere on the board
GND: R2.2, R3.2, TP20.GND (GND1); also elsewhere on the board
unnamed: C1.1, R1.2, R4.2
VB: C3.1, L1.2; also elsewhere on the board



Board: 4 copper layers, 152.4 x 152.4 mm, 208 parts (20 on the bottom side), 87 nets.

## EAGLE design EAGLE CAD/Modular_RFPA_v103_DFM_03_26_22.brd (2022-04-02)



Board: 4 copper layers, 152.4 x 152.4 mm, 189 parts (20 on the bottom side), 85 nets.

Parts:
C1, C7, C111, C112: 22nF; C1206
C2, C3, C4, C5, C6, C8, C9, C10, C11, C12, C22, C101, C102, C103, C104, C105, C106, C107, C109, C110, C113, C114, C201, C207, C208, C209, C210: 0.1uF; 0805_IPC-7351B
C13, C14, C15, C16: 47nF; C1206
C17, C18: 0.1uF; C1812
C19, C20, C21, C23, C303, C304: 10uF; C2220_CKG57N
C117: 2.2uF; C2220_CKG57N
C301: 3300uF; EB25D
D1: DO41Z10
D301: SMC
H1, H2, H3, H4: MOUNT-PAD-SQUARE3.2; 3,2-PAD-SQUARE
IC201: 74AHC1G14DBV; SOT23-5
IC202: LM324D; SO14
IC301, IC302: 78XXS
J1: FUSE_2P; 02540121Z
J2: KK_PCFAN; 47053-1000
J101, J102, J201, J202: BNC_EDGE
JP201, JP202: 1X02
L1, L2, L101, L102: 1uH; L1008
L4: 3.3uH; DR127
L5: 22uH; DR127
L6, L7: DR127
LED1, LED2, LED3: LED5MM
Q1, Q2, Q101, Q102: IRF540; TO220BV
Q201: BSS123; SOT23
R1, R2, R3, R7, R14, R15, R16, R20, R32, R33, R34, R35, R36, R37, R38, R39, R117, R118, R119, R120, R121, R122, R123, R124: 1K; R2512
R4, R5, R6, R13, R17, R18, R19, R26, R101, R102, R103, R104, R105, R106, R108, R110, R302, R303: 1K; R1206
R8, R9, R10, R11, R12, R21, R22, R23, R24, R25, R27, R28, R29, R30, R31, R41, R107, R109, R111, R112, R113, R114, R115, R116, R125, R126, R202, R203, R204, R205, R206, R207, R209, R211, R212, R214, R216, R217, R218, R219: 1.0K; 0805_IPC-7351B
R40: 0.33; R1206
R201: RTRIM3299W
R301: P0817V
T1, T2: HP4_TRAFO; HP4
T201, T202: SOT23-BEC
TP1, TP3, TP7, TP9, TP10, TP11, TP12, TP13, TP14, TP15, TP16, TP18, TP19: PROBE_TPTP_5MM; PROBE_TP_5MM
TP2, TP4, TP5, TP6, TP8, TP17: PROBE_TPTP_7P5MM; PROBE_TP_7P5MM
X1: W237-102
X101: HEATSINK_OMNI_DUAL30-75-D; OMNI-UNI-30-75-D

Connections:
+5V: C16.1, C22.1, IC201.5, IC302.OUT, LED1.A, LED3.A, R29.1, R201.3
+12V: C15.1, C210.1, IC202.4, IC301.OUT, J2.2, LED2.A, T201.C
ABN1: R6.1, R13.1, R101.1, R103.1, T1.11, TP18.TP
ABP1: R19.1, R26.1, R102.1, R104.1, T1.1, TP19.TP
AN2: C103.2, R103.2, R105.1
AN3: C103.1, L101.1, R108.2, R111.1, R113.1
AN4: L101.2, Q101.G, R113.2, R115.1, R117.1, R118.1, TP3.TP
AN5: Q101.S, R34.1, R35.1, R121.1, R123.1, R125.1, TP6.TP
AN6: C113.1, R125.2, TP15.TP
AP2: C105.2, R104.2, R106.1
AP3: C105.1, L102.1, R110.2, R112.1, R114.1
AP4: L102.2, Q102.G, R114.2, R116.1, R119.1, R120.1, TP1.TP
AP5: Q102.S, R32.1, R33.1, R122.1, R124.1, R126.1, TP5.TP
AP6: C114.1, R126.2, TP14.TP
BN2: C5.2, R5.1, R6.2
BN3: C5.1, L1.1, R4.2, R8.1, R9.1
BN4: L1.2, Q2.G, R1.1, R7.1, R8.2, R10.1, TP9.TP
BN5: Q2.S, R2.1, R3.1, R11.1, R36.1, R37.1, TP10.TP
BN6: C2.1, R11.2, TP17.TP
BP2: C11.2, R18.1, R19.2
BP3: C11.1, L2.1, R17.2, R21.1, R22.1
BP4: L2.2, Q1.G, R14.1, R20.1, R21.2, R23.1, TP7.TP
BP5: Q1.S, R15.1, R16.1, R24.1, R38.1, R39.1, TP8.TP
BP6: C8.1, R24.2, TP16.TP
DRAINS_NEG: C1.2, C18.2, C111.2, L7.1, Q2.D, Q101.D, T2.8, TP4.TP
DRAINS_POS: C7.2, C17.2, C112.2, L6.1, Q1.D, Q102.D, T2.6, TP2.TP
GBIAS: R12.1, R25.1, R107.1, R109.1, R218.2, R219.2, T201.E, T202.E, TP11.TP
GND: C2.2, C3.2, C4.2, C6.2, C8.2, C9.2, C10.2, C12.2, C13.2, C14.2, C15.2, C16.2, C19.2, C20.2, C21.2, C22.2, C23.2, C102.2, C104.2, C106.2, C107.2, C109.2, C110.2, C113.2, C114.2, C201.2, C207.2, C208.2, C210.2, C301.-, C303.2, C304.2, D301.A, H1.B3,2, H2.B3,2, H3.B3,2, H4.B3,2, IC201.3, IC202.11, IC301.GND, IC302.GND, J2.1, J101.G1, J101.G2, J101.G3, J101.G4, J102.G1, J102.G2, J102.G3, J102.G4, J202.G1, J202.G2, J202.G3, J202.G4, Q201.2, R2.2, R3.2, R5.2, R13.2, R15.2, R16.2, R18.2, R26.2, R27.2, R28.2, R31.2, R32.2, R33.2, R34.2, R35.2, R36.2, R37.2, R38.2, R39.2, R101.2, R102.2, R105.2, R106.2, R121.2, R122.2, R123.2, R124.2, R201.1, R204.2, R211.2, R212.1, T1.10, T2.9, T202.C, TP1.GND, TP2.GND, TP3.GND, TP4.GND, TP5.GND, TP6.GND, TP7.GND, TP8.GND, TP9.GND, TP10.GND, TP11.GND, TP12.GND, TP13.GND, TP14.GND, TP15.GND, TP16.GND, TP17.GND, TP18.GND, TP19.GND, X1.2, X101.P1, X101.P2
unnamed: IC202.1, R216.1, R217.1
unnamed: R217.2, R218.1, T201.B, T202.B
unnamed: IC201.2, J202.C, R204.1
unnamed: C111.1, R117.2, R118.2
unnamed: C106.1, R111.2
unnamed: IC202.6, IC202.7, R209.1, TP12.TP
unnamed: C209.1, R216.2
unnamed: C104.1, R109.2, R110.1
unnamed: C207.1, R214.1
unnamed: C107.1, R112.2
unnamed: C110.1, R116.2
unnamed: C112.1, R119.2, R120.2
unnamed: C102.1, R107.2, R108.1
unnamed: C209.2, IC202.2, R212.2, R214.2, R219.1
unnamed: C208.1, IC202.3, R209.2, R211.1
unnamed: IC202.10, R203.2, R206.1
unnamed: C109.1, R115.2
unnamed: IC202.8, JP202.2, R205.2, R207.1
unnamed: IC202.9, JP202.1, R202.2, R205.1
unnamed: J201.C, JP201.2, R202.1
unnamed: J201.G1, J201.G2, J201.G3, J201.G4, JP201.1, R203.1
unnamed: T1.3, T1.9
unnamed: IC202.5, Q201.3, R207.2
unnamed: IC201.4, Q201.1, R41.2
unnamed: C201.1, IC202.12, R201.2
unnamed: IC202.13, IC202.14, R206.2, TP13.TP
unnamed: R31.1, T1.2, T1.12
unnamed: D1.A, R302.1, R303.1
unnamed: T2.2, T2.12
unnamed: C117.1, T2.1
unnamed: C117.2, J102.C
unnamed: LED2.K, R27.1
unnamed: LED1.K, R28.1
unnamed: C101.1, J101.C
unnamed: C6.1, R4.1, R12.2
unnamed: C4.1, R9.2
unnamed: LED3.K, R41.1
unnamed: C3.1, R10.2
unnamed: C1.1, R1.2, R7.2
unnamed: C12.1, R17.1, R25.2
unnamed: C101.2, T1.6
unnamed: C10.1, R22.2
unnamed: C13.1, IC301.IN, R302.2
unnamed: D301.C, J1.2, R301.1
unnamed: J1.1, X1.1
unnamed: C23.1, C301.+, D1.C, L4.1, R301.2
unnamed: C303.1, L4.2, L5.1, R40.1
unnamed: C9.1, R23.2
unnamed: C14.1, IC302.IN, R303.2
unnamed: C7.1, R14.2, R20.2
unnamed: J2.3, R29.2
unnamed: T2.3, T2.11
unnamed: T1.4, T1.8
unnamed: T2.4, T2.10
VB: C17.1, C18.1, C19.1, C20.1, C21.1, C304.1, L5.2, L6.2, L7.2, R30.1, R40.2
VB_CT: R30.2, T2.5, T2.7
VB_CT1: T1.5, T1.7

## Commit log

2022-04-02 eagle .brd and .sch files
    [DICO_v100.sch, Modular_RFPA_v100.brd, Modular_RFPA_v100.sch, Modular_RFPA_v101.brd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]
2022-04-02 Work on IRF630 PA
    Also add FET_parameters_sheet.csv
    add IRF520 and IRF520N datasheets
    [FET_parameters_sheet.csv, Modular_RFPA_v105.brd, Modular_RFPA_v105.sch]
2022-04-02 Change Ldamp from 150nH to 47nH
    [Modular_RFPA_v105.brd, Modular_RFPA_v105.sch]
2022-04-02 Update component values for gate bias driver
    Change C209 from 220pF to 330pF
    [Modular_RFPA_v105.brd, Modular_RFPA_v105.sch]
2022-04-02 Done testing for today
    Seem to be getting significant loss across baluns
    Measured input balun leakage at ~650nH (primary referred, both secondaries shorted to gnd)
    [Modular_RFPA_v105.brd, Modular_RFPA_v105.sch]
2022-04-04 Assembly variants
    Try adding a couple to the schematic...
    [Modular_RFPA_v105.brd, Modular_RFPA_v105.sch]
2022-04-04 tidy up sims a bit
    Put all models and subcircuits in a separate folder
    Create one file which includes all of them
    Reference that file in each sim
    Also use the "fetprops" files in all the existing simulations
    [TLV2374.DSN, TLV271.DSN]
2022-04-04 more assembly variant work....
    [Modular_RFPA_v105.brd, Modular_RFPA_v105.sch]
2022-04-04 Updated IRF520N and IRF630 designs
    [Modular_RFPA_v105.brd, Modular_RFPA_v105.sch]
2022-04-05 raw scope data dump
    [Modular_RFPA_v105.brd, Modular_RFPA_v105.sch]
2022-04-05 change a couple bias driver components
    need to rework the 01 board like this too
    [Modular_RFPA_v105.brd, Modular_RFPA_v105.sch]
2022-04-05 More schematic editing
    Add DR127 to my library
    More assembly variant component values
    [Modular_RFPA_v105.brd, Modular_RFPA_v105.sch]
2022-04-06 Work on libraries...
    [Modular_RFPA_v105.brd, Modular_RFPA_v105.sch]
2022-04-06 run renumber_sheet, make this v106
    [Modular_RFPA_v106.brd, Modular_RFPA_v106.sch]
2022-04-06 copy "R" variants to "R90"
    [Modular_RFPA_v106.brd, Modular_RFPA_v106.sch]
2022-04-06 More schematic/library changes
    [Modular_RFPA_v106.brd, Modular_RFPA_v106.sch]
2022-04-06 Thermal camera measurements
2022-04-09 stuff for presentation
    [amp_diagram.brd, amp_diagram.sch]
2022-04-09 working on dico again
    [DICO_v100.brd, DICO_v100.sch]
2022-04-09 save eagle and commit again...
    [DICO_v100.brd, DICO_v100.sch]
2022-04-09 DICO layout
    [DICO_giangrandi_flipped_v100.brd, DICO_giangrandi_flipped_v100.sch, DICO_giangrandi_v100.brd, DICO_giangrandi_v100.sch]
2022-04-09 put DICO eagle files in separate folder
    [DICO_giangrandi_flipped_v100.brd, DICO_giangrandi_flipped_v100.sch, DICO_giangrandi_v100.brd, DICO_giangrandi_v100.sch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]
2022-04-10 dico and detector work
    [DICO_giangrandi_flipped_v100.brd, DICO_giangrandi_flipped_v100.sch]
2022-04-12 Resort eagle folder
    Divide RFPA into revA and revB folders
    Delete other versions
    [Modular_RFPA_RevA.brd, Modular_RFPA_RevB.brd, Modular_RFPA_RevB.sch, Modular_RFPA_v100.brd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]
2022-04-12 adding more technologies...
    [Modular_RFPA_RevA.brd, Modular_RFPA_RevA.sch]
2022-04-12 more technologies....
    [Modular_RFPA_RevA.brd, Modular_RFPA_RevA.sch]
2022-04-13 jellybean component values
    [Modular_RFPA_RevA.brd, Modular_RFPA_RevA.sch]
2022-04-13 stop values from reverting on jellybean Rs
    [Modular_RFPA_RevA.brd, Modular_RFPA_RevA.sch]
2022-04-13 Do same for capacitor library
    [Modular_RFPA_RevA.brd, Modular_RFPA_RevA.sch]
2022-04-14 More part attributes....
    [Modular_RFPA_RevA.brd, Modular_RFPA_RevA.sch]
2022-04-14 EXCLUDEs and INCLUDEs
    [Modular_RFPA_RevA.brd, Modular_RFPA_RevA.sch]
2022-04-14 bom-ex export working
    Need to use tab-delimited format due to parts with commas in partno....
    [Modular_RFPA_RevA.brd, Modular_RFPA_RevA.sch, Modular_RFPA_RevA_BOM.csv, Modular_RFPA_RevA_BOM.xlsx]
2022-04-14 Tidying up revA schematic
    [Modular_RFPA_RevA.brd, Modular_RFPA_RevA.sch]
2022-04-14 Finishing off revA S2...
    Rename files and folder
    Fix DRCs errors caused by changing footprints
    [Easy_RFPA_RevA_S2.brd, Easy_RFPA_RevA_S2.sch, Modular_RFPA_RevA_BOM.csv, Modular_RFPA_RevA_BOM.xlsx]
2022-04-14 export schematic and BOM for revA S2
    [Easy_RFPA_RevA_S2_BOM.xlsx]
2022-04-14 Copy S1 to S2
    [Easy_RFPA_RevA_S1.brd, Easy_RFPA_RevA_S1.sch]
2022-04-14 S1 component values
    Change component values for S1
    Also fix a couple in S2
    Export BOM and pdf for S1
    [Easy_RFPA_RevA_S1.brd, Easy_RFPA_RevA_S1.sch, Easy_RFPA_RevA_S2.brd, Easy_RFPA_RevA_S2.sch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]
2022-04-16 Copy revA S2 to new revB S2
    [Easy_RFPA_RevA_S1.sch, Easy_RFPA_RevB_S2.brd, Easy_RFPA_RevB_S2.sch, Modular_RFPA_RevB.sch]
2022-04-16 Work on revB
    revB is basically the same as revA, except will have soldermask and silkscreen. Some components are moved around to make room for labels. Name labels updated in libraries.
    [Easy_RFPA_RevB_S2.brd, Easy_RFPA_RevB_S2.sch]
2022-04-16 Add thermal pads and heatsink clips to schematic
    Also modify bom-ex old.ulp to not ignore parts which lack a package but have a part number
    [Easy_RFPA_RevB_S2.sch]
2022-04-16 Copy the pads and clips to revA S1 and S2
    [Easy_RFPA_RevA_S1.sch, Easy_RFPA_RevA_S2.sch, Easy_RFPA_RevB_S2.sch]
2022-04-17 Better docfield
    I modified my docfield symbol (not included in the repo!)
    I define a few global attributes:
    BOMREV
    FABREV
    AUTHOR
    DRAWING_NUMBER
    [Easy_RFPA_RevB_S2.sch]
2022-04-17 Will have to place sheet names manually...
    [Easy_RFPA_RevB_S2.sch]
2022-04-17 ltspice demo
    writing up the wiki section on ltspice
    also some screenshots
    [TLV2374.DSN, TLV271.DSN]
2022-04-18 re-export boms
    one of the FETs in S1 had irf520n as the value?
    [Easy_RFPA_RevA_S2.brd, Easy_RFPA_RevA_S2.sch]
2022-04-18 Add global attributes and sheet names
    [Easy_RFPA_RevA_S1.sch, Easy_RFPA_RevA_S2.sch, Easy_RFPA_RevB_S2.sch]
2022-04-18 Add modified frames library
2022-04-18 Replace frames and re-print pdfs
    [Easy_RFPA_RevA_S1.sch, Easy_RFPA_RevA_S2.sch, Easy_RFPA_RevB_S2.sch]

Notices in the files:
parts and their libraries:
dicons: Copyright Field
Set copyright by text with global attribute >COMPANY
